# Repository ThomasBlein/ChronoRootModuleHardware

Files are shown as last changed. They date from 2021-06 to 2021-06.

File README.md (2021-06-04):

# ChronoRoot: High-throughput phenotyping by deep learning reveals novel temporal parameters of plant root system architecture

Nicolás Gaggion¹, Federico Ariel², Vladimir Daric³, Éric Lambert³, Simon Legendre³, Thomas Roulé³, Alejandra Camoirano², Diego Milone¹, Martin Crespi³, Thomas Blein³, Enzo Ferrante¹

¹ Research Institute for Signals, Systems and Computational Intelligence (sinc(i)), FICH-UNL, CONICET, Ciudad Universitaria UNL, Santa Fe, Argentina.\
² Instituto de Agrobiotecnología del Litoral (IAL), CONICET, FBCB, Universidad Nacional del Litoral, Colectora Ruta Nacional 168 km 0, Santa Fe, Argentina.\
³ Institute of Plant Sciences Paris-Saclay (IPS2), CNRS, INRA, University Paris-Saclay and University of Paris Bâtiment 630, 91192 Gif sur Yvette, France.

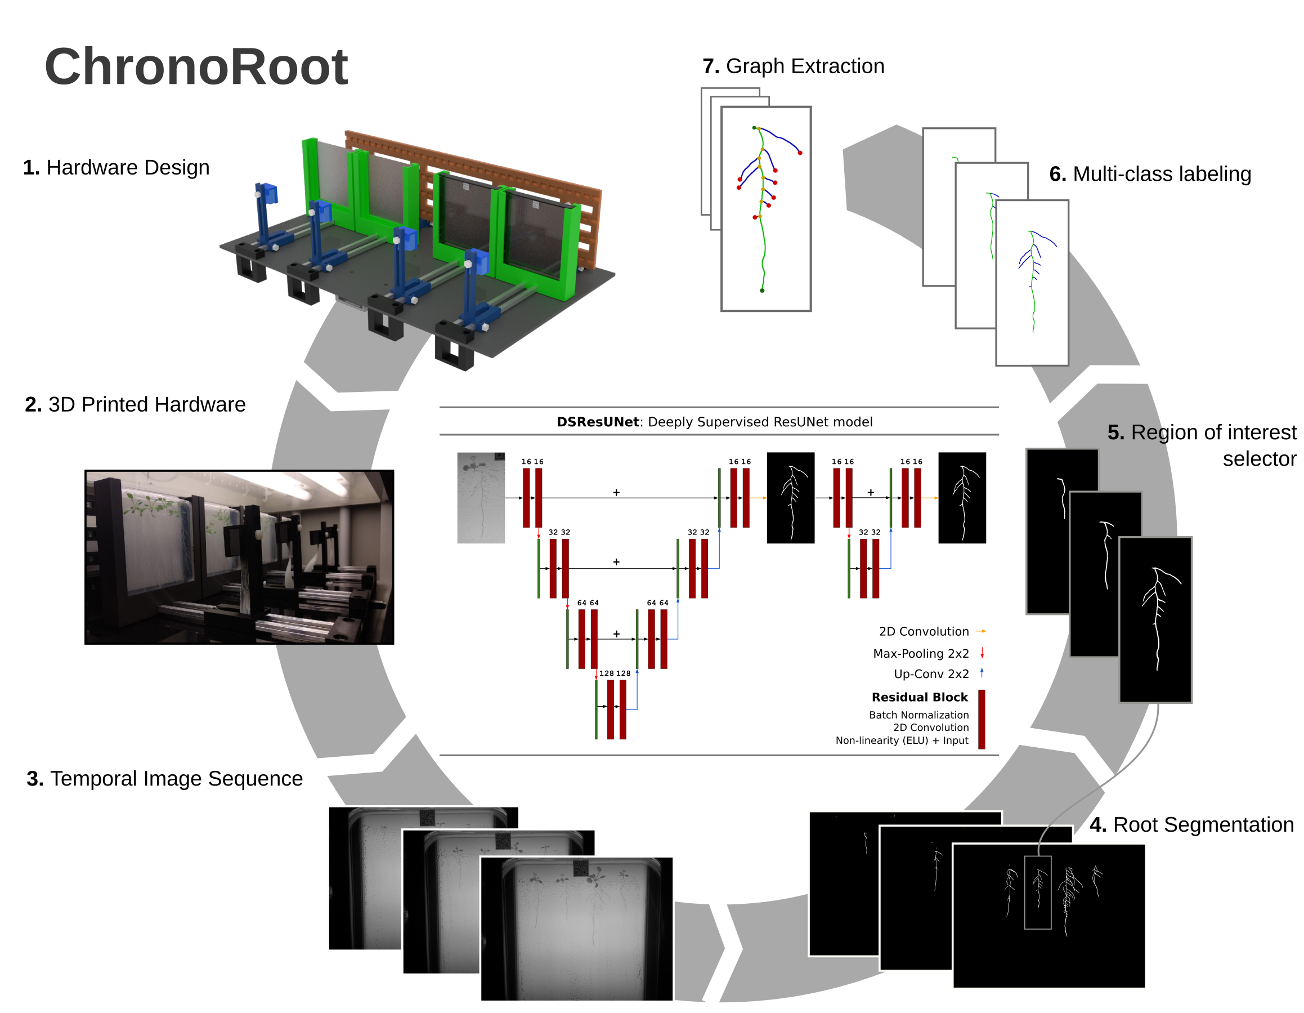
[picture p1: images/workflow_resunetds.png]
ChronoRoot workflow


# ChronoRoot Module Hardware Design

The hardware (3D print and laser cut) of the ChronoRoot module designed
for image-based plant phenotyping.

## ChronoRoot module description

The ChronoRoot device is an affordable and modular imaging system based on 3D-printed
and laser cut pieces and off-the-shelf electronics. Each module consists of a
Raspberry Pi (v3)-embedded computer controlling four fixed-zoom and fixed-focus cameras
(RaspiCam v2), and an array of infrared (IR) LED back-light. In between each camera
and the corresponding IR array, there is a vertical 12 x 12 cm plate for seedling
growth, allowing automatic image acquisition repeatedly along the experiment without any
modification or movement of the imaging setup. The four-plate module is small
(62 x 36 x 20 cm) and can be placed in any growth chamber. The different parts of
the imaging setup (back-light, plate support and camera) can be positioned along
a horizontal double-rail to control the field of view of the camera and accurate lightning.
In addition, the camera can be moved vertically. ChronoRoot allows image
acquisition at a high temporal resolution (a set of pictures every minute). The
use of an IR back-light (850 nm) and optional long pass IR filters (> 830 nm)
allow acquiring images of the same quality independently from the light conditions
required for the experiment, during day and night.

## Description of the module

In this repository, we include the hardware specification and the 3D printing
and laser cutting files needed to build a module. These notes and files are
provided as open-hardware specifications (CERN Open Hardware Licence version 2),
to encourage other scientists to 3D print and mount the device in their own
laboratories.

The module consist of a Raspberry Pi 3 model B with an additional camera multiplexer
module (IVPort V2 Raspberry Pi Camera Module V2 Multiplexer, Ivmech Mekatronik
& İnovasyon Ltd.) and allows to connect four cameras. It is boxed in a cage
fixed under the main board.

### Low-cost device for automatic image acquisition of plant plates. 3D rendering of a ChronoRoot module.

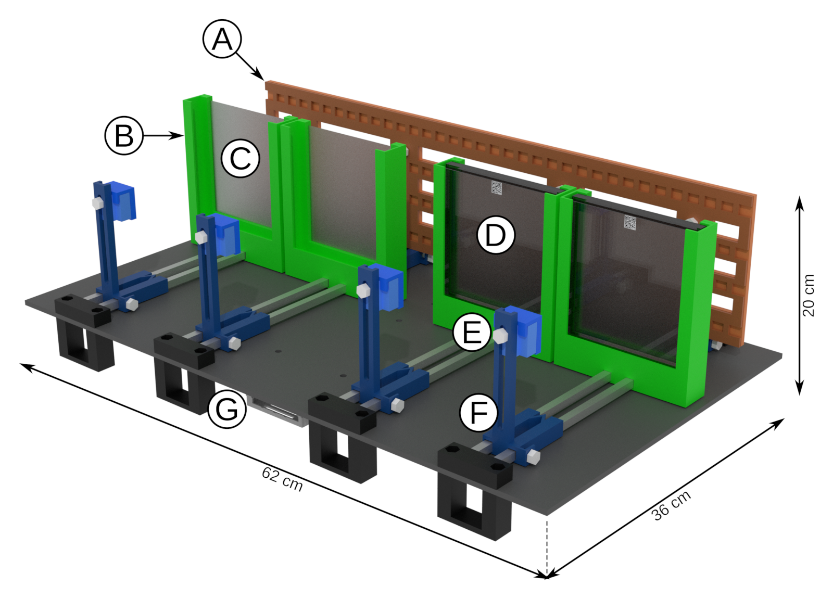
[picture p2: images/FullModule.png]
ChronoRoot module


(A) mobile and controlled infrared (IR) backlight (850 nm), (B) mobile plate
support, (C) diffusing filter, (D) 12 cm x 12 cm square plate with QR code on
the top, (E) Camera case equipped with an IR long pass filter (> 830 nm), (F)
mobile camera support, (G) Raspberry Pi computer controlling the module (IR
backlight and camera).  The NIR illumination was build with four rows of LED
flexible tape (tri-chip SMD5050-150-IR 850 nm, Huake LTD, China) fixed in
a sandwich between two acrylic plates (580 mm x 140 mm x 3 mm) laser cuts to
allow air flow and prevent the LED strip from ungluing. The four strips of LED
were connected in parallel to a 12V AC/DC adaptor fixed under the module. The
power supply cable of the adaptor is under the control of relay (Single Relay
Board #27115, Parallax Inc), in a box fixed near the adaptor. It allows the
control of the NIR illumination by the computer. The LED array is maintained
vertically by L-shaped supports able to move along the aluminum horizontal axes
as four individual panels in the module, corresponding to the respective plant
plates.

### LED near-infrared panel

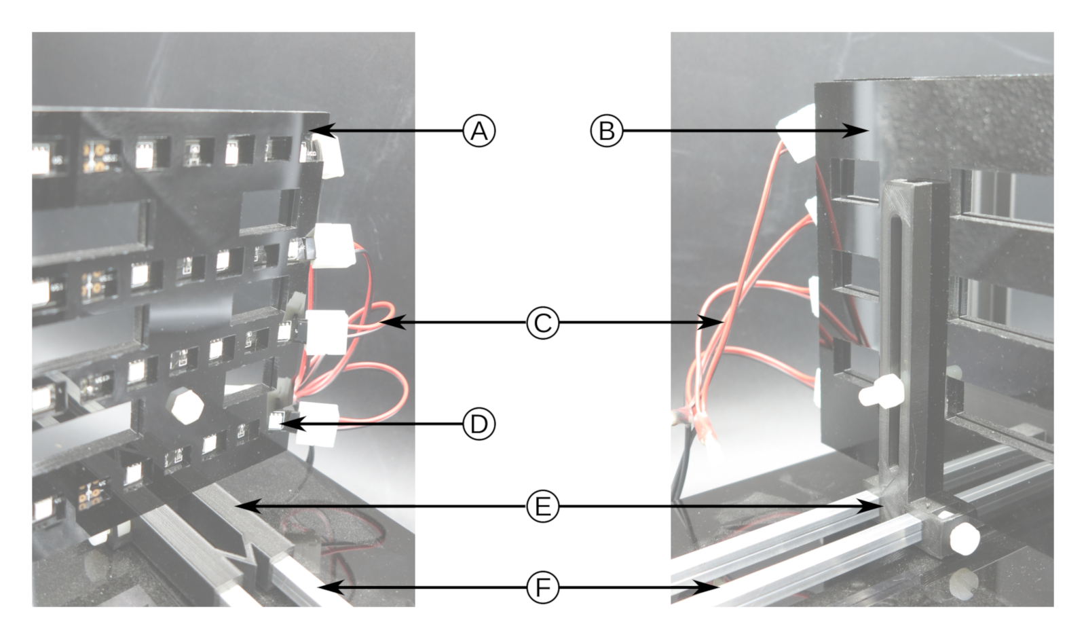
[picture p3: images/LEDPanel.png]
ChronoRoot NIR LED panel


Front view (left) and back view (right). The LED strips (D) are squeezed in
between two acrylic panels (A and B) to prevent them from unsticking from the
back panel. The strips are linked in parallel to the AC/DC adaptor through strip
connector (C). The full LED panel is kept in vertical position via an L-shaped
support (E) able to move along the double aluminum axis (F). Acrylic screws and
nuts are used to maintain the LED panel on the L-shape support and fixed the
horizontal position on the horizontal axis. U-shaped plate holders were designed
to hold 12.5 cm x 12.5 cm square petri dishes used to grow the plants. The plate
holder carries a diffusion filter (Cinegel R3000 Tough Rolux, Rosco Laboratories
Inc.) at the back of the plate to allow homogeneous backlight illumination of
the plates by the NIR LED array.  The four plate holders can be moved
independently along their respective horizontal axis.

### Plate support

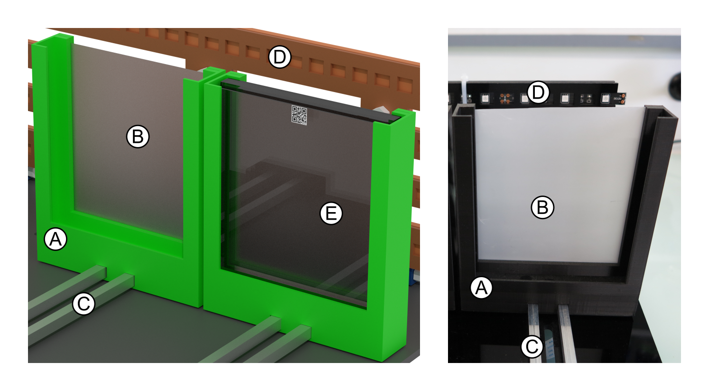
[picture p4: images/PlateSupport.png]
ChronoRoot plate support


Annotated 3D rendering (left) and picture (right) of the plate support. The
U-shaped plate support (A) carries a diffusion filter at the back (B) allowing
an homogeneous near-infrared illumination. Each support moves horizontally on
the double axis (C). A classical 12.5 cm x 12.5 cm square plate fit into the
plate support (E).  Each camera is a regular Raspberry Pi NoIR V2 module (Sony
IMX219 8-megapixel sensor) which is able to capture NIR wavelengths in addition
to the classical visible spectrum. It is positioned in a box that can be moved
vertically on an L-shaped support which can be shifted along the horizontal
axis. The focus of the camera is adjusted manually before the start of the
experiment by turning the objective lens using the provided crown. To be able to
record pictures exclusively from the NIR spectrum, an IR long pass filter (12.5
mm diameter, RG830 Schott AG) can be positioned in front of the camera to
exclude light below 830 nm and provide consistent images independently of the
lightning of the growth chamber.

### The camera setup

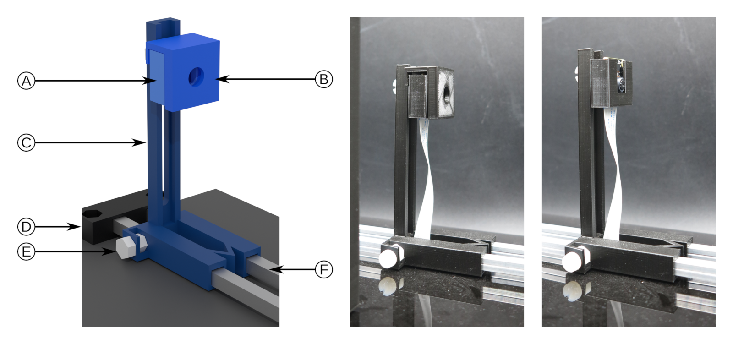
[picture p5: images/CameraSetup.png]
ChronoRoot camera setup


(Left) annotated 3D rendering; (middle) camera on a module carrying a filter;
(right) camera on a module without the filter. A Raspberry Pi NoIR V2 module is
enclosed in a 3D printed box (A) that could carry an optional filter (B). The
box can be moved vertically on an L-shaped support (C) which itself is able to
move along a double aluminum axis (F); The position of the L-shape support and
of the camera box are secured by acrylic screw and nut (E for L-shaped support).
The double aluminum axis is attached to the main board by a 3D printed part (D).

### Electronic connection of a module.

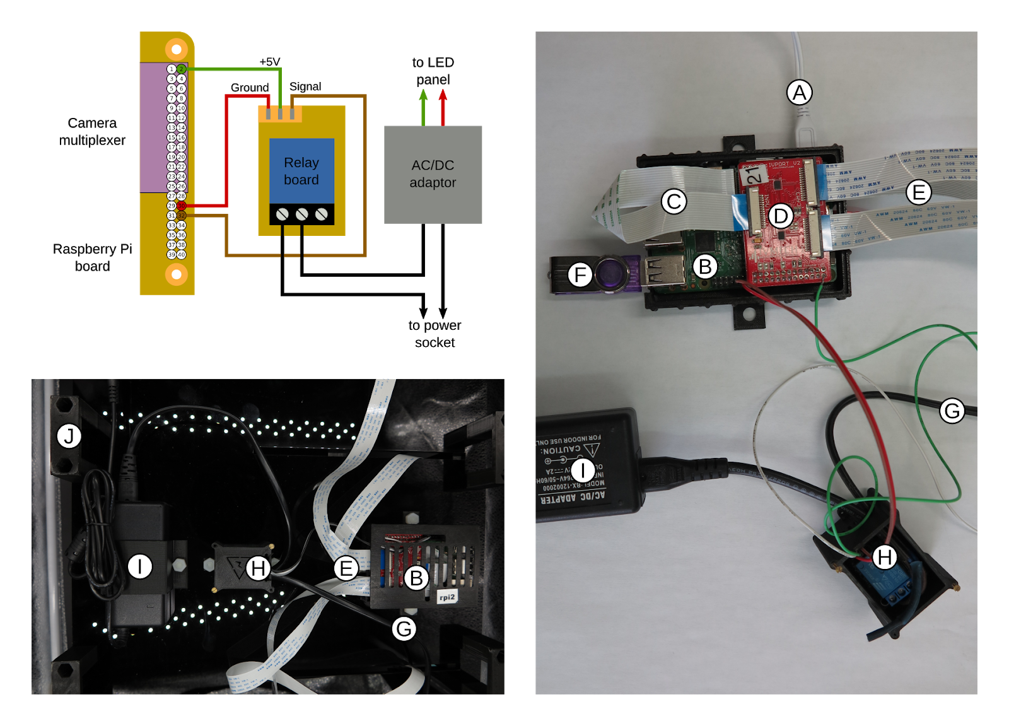
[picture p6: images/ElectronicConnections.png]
ChronoRoot electronic connection


Schematic electric connection between the Raspberry Pi GPIO, the camera
multiplexer, the relay board and AC/DC adaptor (up left). Real view of the
connection with different part boxes open (right). The Raspberry Pi (B) is
connected to a USB power adaptor (A). The camera multiplexer module (D) is
plugged on the Raspberry Pi GPIO port and connected to the Raspberry Pi camera
by a strip (C). Each camera is connected to the multiplexer by a strip (E). The
pictures are saved on a USB stick (F) or a USB hard drive directly connected to
the Raspberry Pi. A relay board (H) is connected to the Raspberry Pi GPIO and
controls the main power (G) of the AC/Dc adaptor powering the LED strip. The
final organization of the controlling part under the module main board raised by
foots (J).

# ChronoRoot Module Controler

Software for image aquisition on the module available on the [ChronoRoot Module Controler repository](https://github.com/ThomasBlein/ChronoRootControl)

# Image analysis

Software for image analysis available on the [ChronoRoot repository](https://github.com/ngaggion/ChronoRoot/)

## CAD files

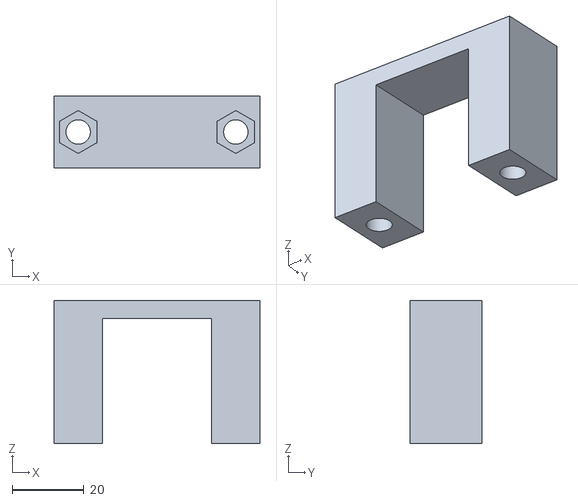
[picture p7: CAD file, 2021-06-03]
01_MainBoard/main_board_foot.stl
57.5 x 20.0 x 40.0

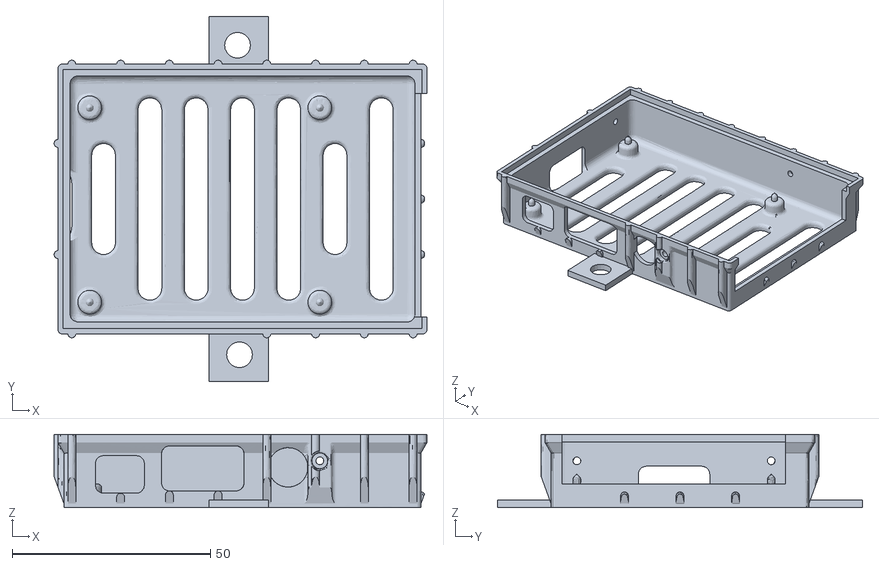
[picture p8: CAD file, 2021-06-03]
01_MainBoard/RaspberryPi_Case 1.stl
94.0 x 92.0 x 18.5

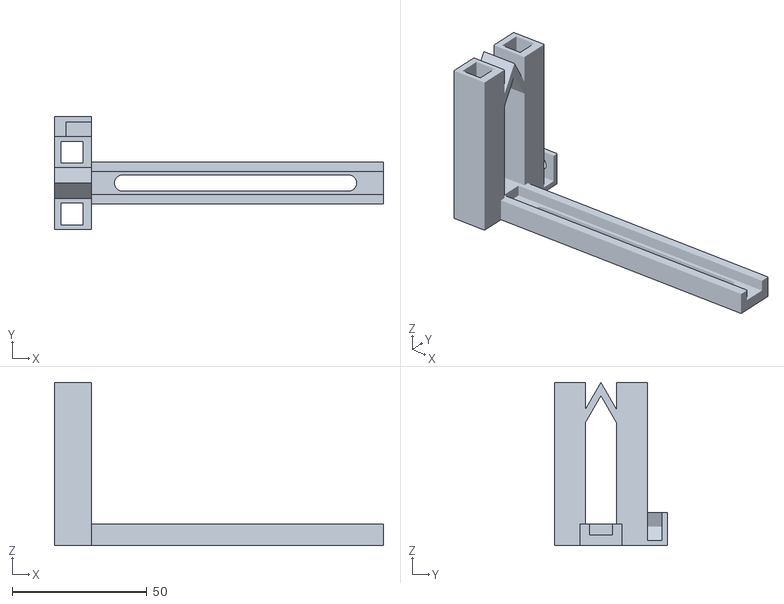
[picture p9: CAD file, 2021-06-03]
02_LED/mobile_L_shaped_support.stl
122.3 x 42.0 x 60.7

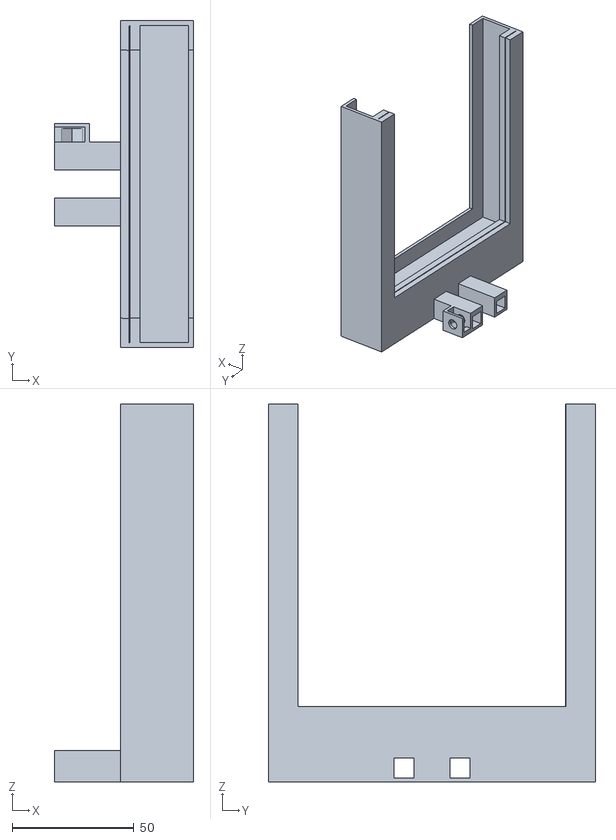
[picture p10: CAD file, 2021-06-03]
03_PlateSupport/mobile_plate_support.stl
57.0 x 134.0 x 155.0

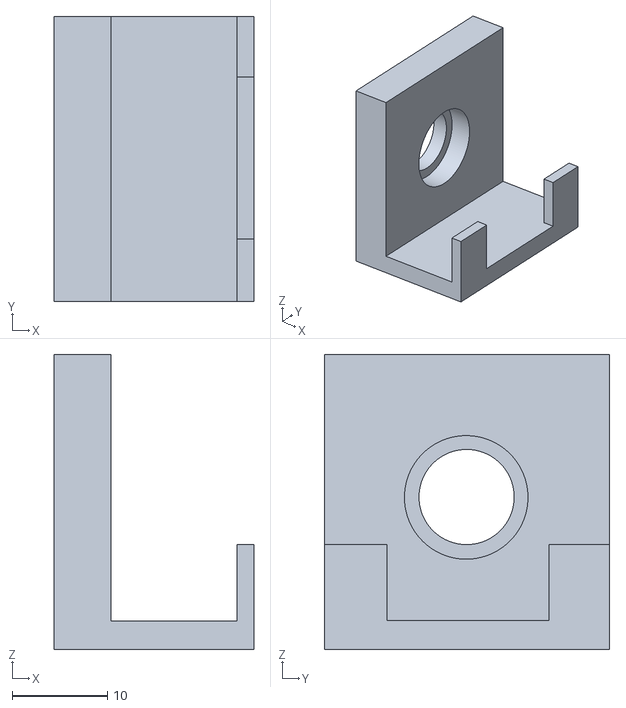
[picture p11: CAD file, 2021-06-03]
04_camera/filter_support.stl
21.0 x 30.0 x 31.0

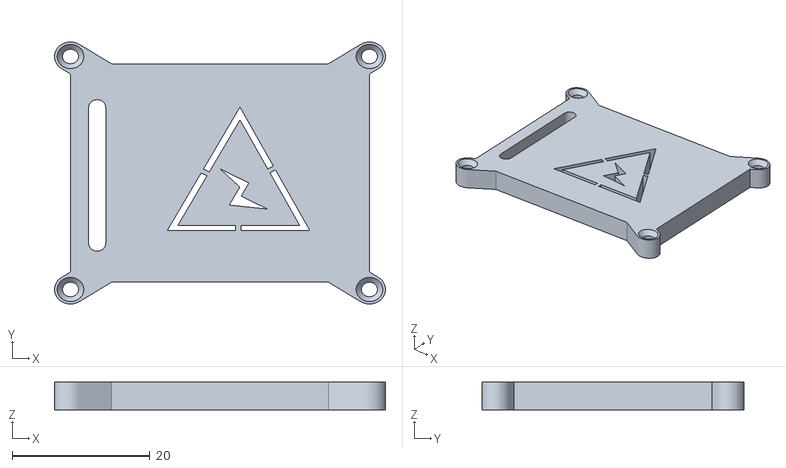
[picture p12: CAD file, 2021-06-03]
01_MainBoard/relais_box_cover.stl
48.0 x 38.0 x 4.00

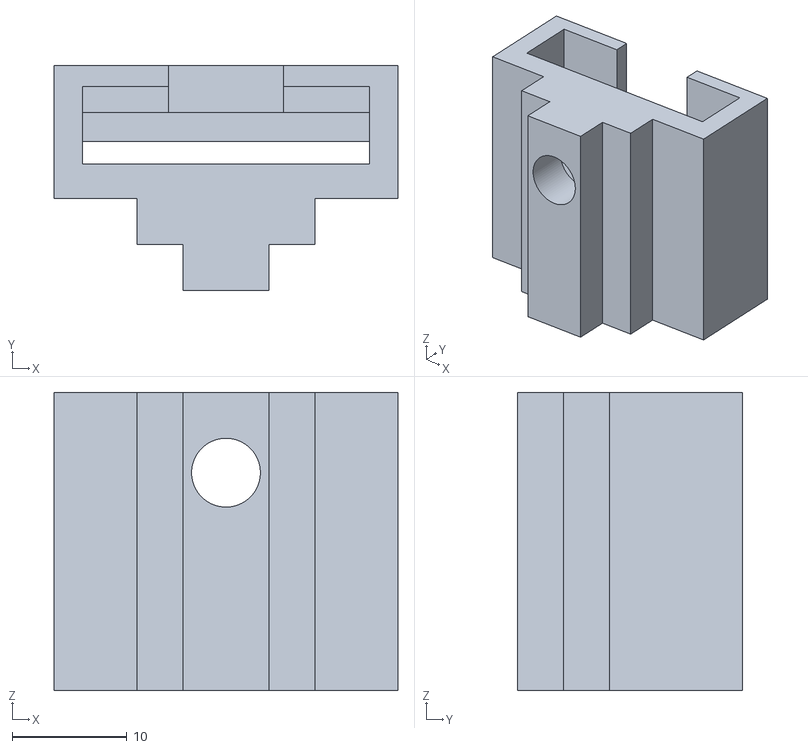
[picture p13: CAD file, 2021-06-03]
04_camera/camera_handler.stl
30.0 x 19.6 x 26.0

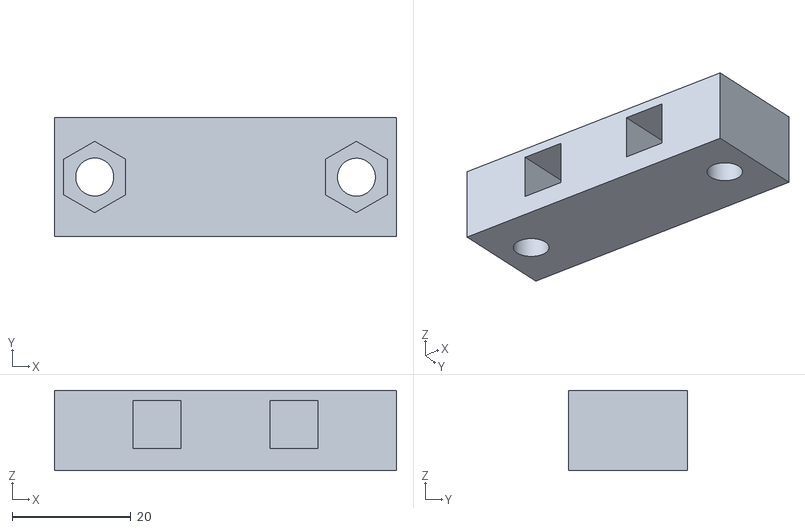
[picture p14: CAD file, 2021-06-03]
01_MainBoard/axis_holder.stl
57.5 x 20.0 x 13.5

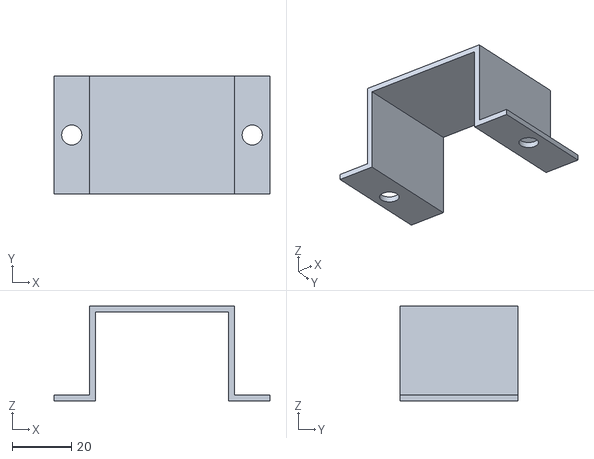
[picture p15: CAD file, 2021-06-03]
01_MainBoard/ACDC_adaptor_support.stl
73.0 x 40.0 x 32.0

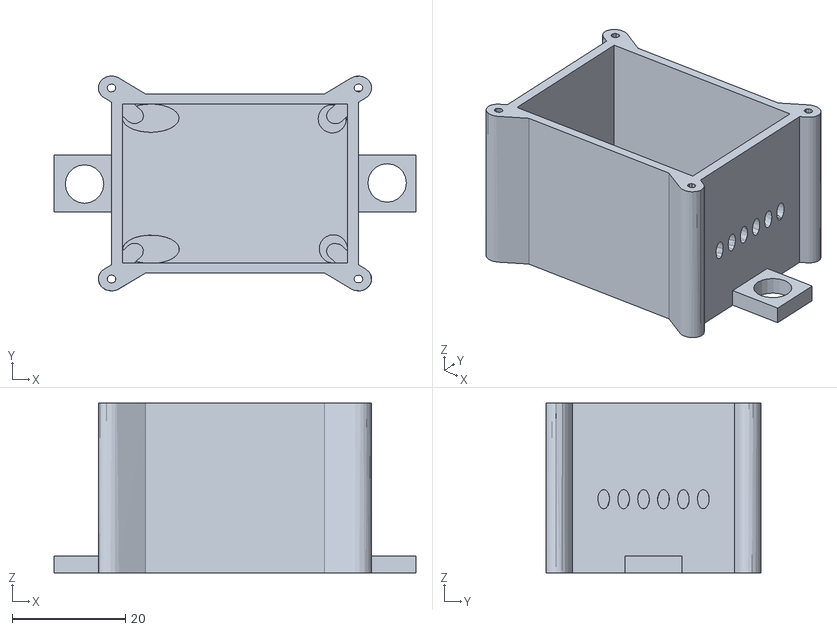
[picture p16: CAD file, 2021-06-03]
01_MainBoard/relais_box.stl
64.0 x 38.0 x 30.0

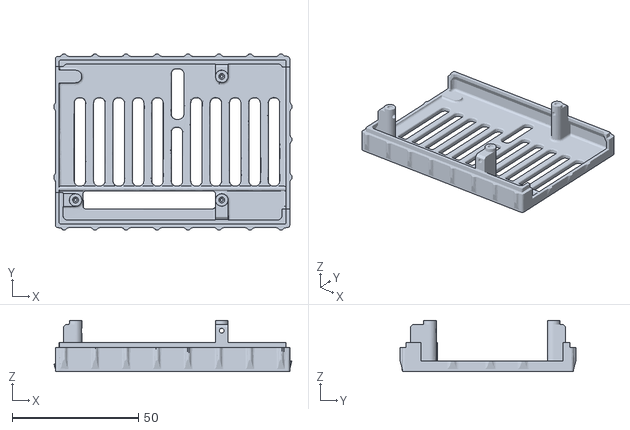
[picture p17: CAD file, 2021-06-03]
01_MainBoard/rasberryPi-top mod.stl
94.4 x 70.0 x 20.3

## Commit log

2021-06-03 First public version of ChronoRoot Hardware
    [ACDC_adaptor_support.stl, RaspberryPi_Case 1.stl, axis_holder.stl, camera_handler.stl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]
2021-06-04 fix: correct figure for the camera setup
